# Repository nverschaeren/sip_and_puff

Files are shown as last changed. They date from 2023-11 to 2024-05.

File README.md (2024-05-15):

# sip_and_puff
A sip and puff device to control your computer

## Problem setting 

When interviewing visitors using our web platform with alternative input devices the sip and puff device showed up several times. A check online showed these devices are selling for at least 250 Euro, but easily do more than a thousand.

To have such a device available to test, but also create a way to let people who depend on such devices to use our site this project we will investigate, design, program and build such a device. The target is to have it available for around 10 Euros.

## Initial setup

The base setup will run on an Arduino Pro Micro (replaced the Arduino Nano with a Arduino Pro Micro as that one has Keyboard support).
A tube will be connected to 4 sensors that can detect sip and puff actions, that can bring the user 8 different actions that the arduino can translate into keyboard actions and send to the computer via USB. Also combinations of sip and puff actions can be combined to add more actions.

As moist should be prevented from entering the sensors Anti-tar cigarette filters should be placed on the inlets. A filter will be ok for about a week of usage and should be replaced after.

To create create a tight connection for the tar-filter mouht pieces I used heat-proof electric-wire insulation tape, cut in half and wrap arround the inlets twice. The tape needed replacedment after a year of usage.

## Base prices

Prices checked on 9 Februari 2023 all including shipping. Mostly using AliExpress

### Fixed prices:
- Arduino Pro Micro (32u4): € 4,98
- HX710b pressure sensor (PSG010R) (4x): € 1,24
- 2m Cable micro usb: € 1,15
- LED (2x): € 0,04

Total fixed costs: 11,17

### Dynamic prices:
- PLA: € 0,05 meter
- 28AWG cable: € 0,22 meter
- Silicon tube (food save): € 1,07 meter
- Anti-tar cigarette filters (100): € 8,50
- heat-proof electric-wire insulation tape (10cm): € 0,02

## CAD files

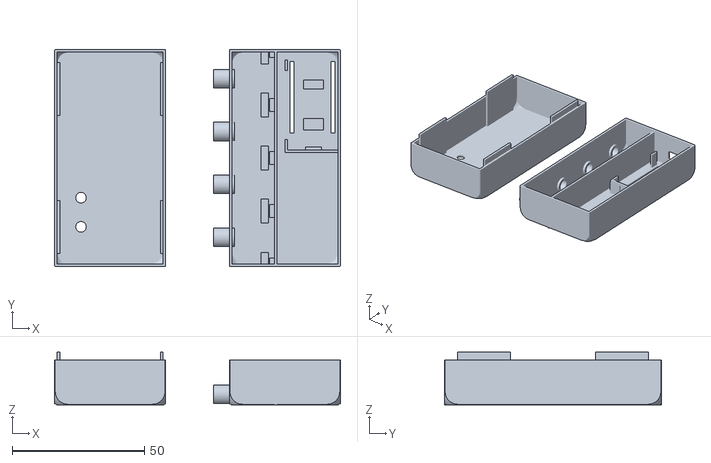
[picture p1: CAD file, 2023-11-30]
3D_print/sip_puff_full.stl
108.0 x 82.0 x 20.0

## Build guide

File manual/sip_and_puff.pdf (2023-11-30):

# Sip & Puff setup for MacOs

## Adding switch actions to the mouthpieces

The Sip & Puff device works with switch-control in MacOs. A few actions use regular key-strokes, and for a few we need to set-up
specific switch controls to make browsing
faster and easier.
1. Go to system preferences and choose Accessibility
2. Now turn on “Switch Control”
3. The Switch control modal will appear on screen
4. Now connect the sip & puff device to
an USB port of your Macbook

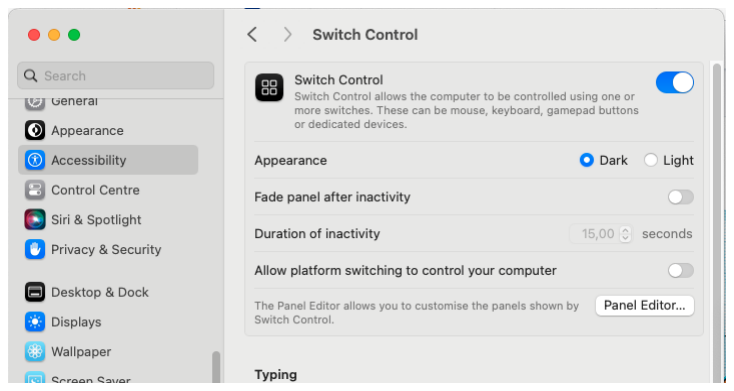
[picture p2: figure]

5. Scroll down in the “Switch control” modal, and find “Switches”
6. If no “Space Input” switch is listed add a new Switch by clicking +
7. When a switch is requested, puff on the most left mouthpiece
8. Then select “Select item” as action
9. Click + again to add a new switch
10. Puff on the second mouthpiece from the
left when a switch is requested
11. Select “Move To Next Item” as action
12. Click + again to add a new switch
13. When a switch is requested, sip on the most left mouthpiece
14. Select “Restart from top” as action
15. Click + again to add a new switch
16. When a switch is requested, sip on the
3rd mouthpiece from the left
17. Select “Open application…” as action

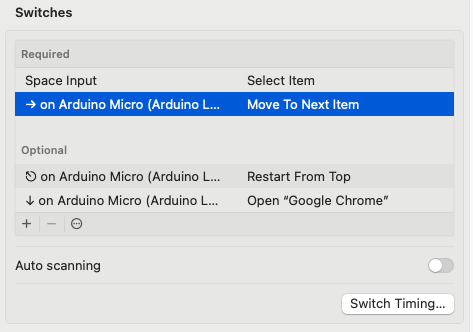
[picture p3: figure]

18. in the Finder popup select Google Chrome in your application folder
19. The switch actions should now contain 4 items

# Sip and Puff

1 | 2 | 3 | 4
O | O | O | O
1. Sip: | return to top
Puff: | select item

## 2. Sip: Press

Puff: | Next item
3. Sip: | Open Google Chrome

## Puff: Press

## 4. Sip: Press

## Puff: Press

: Switch control | : Google Chrome browser

When the red light is on the Sip & Puff device is calibrating and no Sip or Puff actions are recorded

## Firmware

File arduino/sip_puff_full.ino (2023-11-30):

#include <Q2HX711.h>
#include "Keyboard.h"
// #include "Mouse.h"

/* connect the sensors to pin 2-9 */
Q2HX711 SENSOR_01(2, 3);
Q2HX711 SENSOR_02(4, 5);
Q2HX711 SENSOR_03(6, 7);
Q2HX711 SENSOR_04(8, 9);
 
/* sensor state: 0 neutral, 1 sipp, 2 puff */
int sensorStates [] = {0, 0, 0, 0};

/* initial sensor value */
int sensorInitValues [] = {0, 0, 0, 0};

/* calibration led */
int calibrationLed = 14;

/* sip-puff detection led */
int actionLed = 15;

/* calibration counter */
int calibrationCounterInitial = 500;
int calibrationCounter = 2;
bool calibrating = false;

/* CTRL key */
/* OSX: */
char ctrlKey = KEY_LEFT_GUI;
/* Windows and Linux: */
// char ctrlKey = KEY_LEFT_CTRL;

/* debug modus set to true to test sensors */
bool debug = false;

void setup() {
  if (debug) {
    Serial.begin(9600);
  }
  pinMode(calibrationLed, OUTPUT);
  pinMode(actionLed, OUTPUT);
  Keyboard.begin();
  calibrate();
}

void loop() {
  if (!calibrating) {
    updateSensorState(0, SENSOR_01.read() / 10000 );
    delay(10);
    updateSensorState(1, SENSOR_02.read() / 10000 );
    delay(10);
    updateSensorState(2, SENSOR_03.read() / 10000 );
    delay(10);
    updateSensorState(3, SENSOR_04.read() / 10000 );
    delay(10);
    sendKeys();
    calibrationCounter--;
    if (calibrationCounter == 0) {
      calibrationCounter = calibrationCounterInitial;
      calibrate();
    }
  }
  delay(100);
}

void calibrate() {
  calibrating = true;
  delay(300);
  digitalWrite(calibrationLed, HIGH);
  sensorInitValues[0] = SENSOR_01.read() / 10000;
  delay(100);
  sensorInitValues[1] = SENSOR_02.read() / 10000;
  delay(100);
  sensorInitValues[2] = SENSOR_03.read() / 10000;
  delay(100);
  sensorInitValues[3] = SENSOR_04.read() / 10000;
  delay(100);
  digitalWrite(calibrationLed, LOW);
  calibrating = false;
}

void updateSensorState(int sensor, int curValue) {
  int state_sensor = sensorStates[sensor];
  int init_val_sensor = sensorInitValues[sensor];
  if (state_sensor == 0) {
    if (curValue < init_val_sensor - 10) {
      /* Sip detected */
      sensorStates[sensor] = 1;
    }
    if (curValue > init_val_sensor + 10) {
      /* puff detected */
      sensorStates[sensor] = 2;
    }
  } else if (state_sensor == 1 or state_sensor == 2) {
    /* sip or puff state ended */
    sensorStates[sensor] = 0;
  }
}

void sendKeys() {
  // Keyboard.press(KEY_LEFT_SHIFT);
  // Keyboard.press(KEY_LEFT_ALT);
  switch (sensorStates[0]) {
    case 1:
      // sip 1
      digitalWrite(actionLed, HIGH);
      keyboardSend(KEY_ESC, "ESC");
      break;
    case 2:
      // puff 1
      digitalWrite(actionLed, HIGH);
      keyboardSend(0x20, "SPACE"); // SPACE
      //Mouse.move(0, +40);
      break;
    default:
      break;
  }
  switch (sensorStates[1]) {
    case 1:
      // sip 2
      digitalWrite(actionLed, HIGH);
      keyboardSend(KEY_RETURN, "RETURN");
      break;
    case 2:
      // puff 2
      digitalWrite(actionLed, HIGH);
      keyboardSend(KEY_RIGHT_ARROW, "RIGHT");
      // Mouse.move(+40, 0);
      break;
    default:
      break;
  }
  switch (sensorStates[2]) {
    case 1:
      // sip 3
      digitalWrite(actionLed, HIGH);
      keyboardSend(KEY_DOWN_ARROW, "DOWN");
      break;
    case 2:
      // puff 3
      digitalWrite(actionLed, HIGH);
      keyboardSend(KEY_BACKSPACE, "BACKSPACE");
    default:
      break;
  }
  switch (sensorStates[3]) {
    case 1:
      // sip 4
      digitalWrite(actionLed, HIGH);
      keyboardSend(KEY_LEFT_SHIFT, "LEFT");
      delay(10);
      keyboardSend(KEY_TAB, "TAB");
      break;
    case 2:
      // puff 4
      digitalWrite(actionLed, HIGH);
      keyboardSend(KEY_TAB, "TAB");
      break;
    default:
      break;
  }
  delay(100);
  Keyboard.releaseAll();
  digitalWrite(actionLed, LOW);
}

void keyboardSend(char key, char* keyLabel) {
  if (debug) {
    Serial.print(keyLabel);
    Serial.println();
  } else {
    Keyboard.press(key);
  }
}

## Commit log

2023-11-30 Sip and puff version 2
    [sip_puff_full.stl]
2024-05-15 Update README.md
    Added information about the electric-insulation tape used to tight connect the tar-filter mouth pieces
